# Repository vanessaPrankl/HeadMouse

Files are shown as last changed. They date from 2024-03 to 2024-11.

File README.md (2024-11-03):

# HeadMouse
 
This project provides hardware, enclosure and software for the head-motion based computermouse HeadMouse.



## Hardware
A BOM and PCB-files are provided in the hardware folder. A 600mAh LiPo-battery has been used for the prototyping, the battery only lasts for 3.5h in this case which is mainly caused by the high power consumption of the ESP32-S3-WROOM buetooth module. 



## Software
The following external libraries are utilized:
| Library | Provider | Licence |  
|------|----------|---------|
| [BleMouse](https://github.com/T-vK/ESP32-BLE-Mouse) | [T-vK](https://github.com/T-vK) | MIT License |
| [AdafruitBNO055](https://github.com/adafruit/Adafruit_BNO055) | [Adafruit](https://github.com/adafruit) | MIT License |
| [ESP32_TimerInterrupt](https://github.com/khoih-prog/ESP32TimerInterrupt) | [khoih-prog](https://github.com/khoih-prog) | MIT License|

Additionally, a HeadMouse library including major HeadMouse functions is provided. 



The hardware pins are configured in the hm_board_config_v1_0.hpp file of the headmouse library.
The default preferences are set in default_preferences.hpp (include folder of project).

## Enclosure
The enclosure consists of 2 3D-printed parts, 2 screws and according nuts for assembly and a sticky clip for mounting the deivce on the user's head. 



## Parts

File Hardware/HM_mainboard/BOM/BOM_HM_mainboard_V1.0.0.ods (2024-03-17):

Reference | Value | Digikey | Mouser | Reichelt | Menge | Datasheet
AC1 | LSM6DSOXTR |  | LSM6DSOXTR |  | 1 | https://www.st.com/resource/en/datasheet/lsm6dsox.pdf
C1, C4 | 4.7uF |  | 81-GRM188Z71A475KE5J |  | 2 | ~
C2, C3, C10, C19 | 1.0uF-25V-(+80/-20%) |  | 647-F921E105KPA |  | 4 | ~
C5, C6 | 15pF-1% |  | 80-C0603C150F8HAUTO |  | 2 | ~
C7 | 22uF |  | 81-GRM188R60J226ME0J |  | 1 | ~
C8, C9, C11-C18, C20 | 100nF | 1276-CL10B104KB8NNNLCT | 581-06035C104K4 |  | 11 | ~
D1 | 10BQ015 |  | 78-VS-10BQ015-M35BT |  | 1 | https://eu.mouser.com/ProductDetail/Vishay-Semiconductors/VS-10BQ015-M3-5BT?qs=asPD7ZL2j3VpzaHhlDLLKA%3D%3D&gad_source=1
D2 | WE-TVS-824015 |  | 710-824015 |  | 1 | https://www.we-online.com/components/products/datasheet/824015.pdf
D3, D4 | 155124RV73200 |  | 710-155124RV73200 |  | 2 | https://www.we-online.com/components/products/datasheet/155124RV73200.pdf
FL1 | WE-CNSW 744232090 |  | 710-744232090 |  | 1 | https://www.we-online.com/components/products/datasheet/744232090.pdf
J1 | JST PH2P ST90 |  |  | JST PH2P ST90 | 1 | https://www.reichelt.at/at/de/jst-stiftleiste-90-1x2-polig-ph-jst-ph2p-st90-p185056.html?PROVID=2807
J2 | USB4105-GF-A |  | 640-USB4105-GF-A |  | 1 | https://www.mouser.at/ProductDetail/GCT/USB4105-GF-A?qs=KUoIvG%2F9IlY%2FMLlBMpStpA%3D%3D&gad_source=1
J3 | Conn_01x04 |  | Stiftleiste, Raster: 2.54mm |  | 1 | ~
J4-J7 | 54-00174 | 839-54-00174CT |  |  | 4 | https://tensility.s3.amazonaws.com/uploads/pdffiles/54-00174.pdf?X-Amz-Expires=600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
Q1 | PMV27UPEAR | 4530-AS3401CT | 771-PMV27UPEAR |  | 1 | https://mm.digikey.com/Volume0/opasdata/d220001/medias/docus/2779/AS3401.pdf
R1 | 10k/1% |  | 660-RN73H1JT1002F100 |  | 1
R2 | 2k |  | 71-CRCW06032K00FKEAC |  | 1
R3, R4, R7, R12-R14 | 10k/1% |  | 660-RN73H1JT1002F100 |  | 6
R5, R6 | 5k1 |  | 791-RMC1/16K5101FTP |  | 2
R8-R11 | 120 |  | 603-RC0603FR-10120RL |  | 4
S1, S2 | SW_Push |  | 179-TS046643BK160SMT |  | 2 | https://www.mouser.at/datasheet/2/358/typ_6x6_mm_tact_switches-1275689.pdf
S3 | 450404015514 |  | 710-450404015514 |  | 1 | https://www.we-online.com/components/products/datasheet/450404015514.pdf
U1 | MCP73831-2 |  | 579-MCP73831T-2ACIOT |  | 1 | http://ww1.microchip.com/downloads/en/DeviceDoc/20001984g.pdf
U2 | TC1262-33 |  | 579-TC1262-3.3VDBTR |  | 1 | http://ww1.microchip.com/downloads/en/DeviceDoc/21373C.pdf
U3 | ESP32-S3-WROOM-1 |  | 356-ESP32-S3WRM1N8R2 |  | 1 | https://www.espressif.com/sites/default/files/documentation/esp32-s3-wroom-1_wroom-1u_datasheet_en.pdf
U4 | WE-TVS-824015043 |  | 710-824015043 |  | 1 | https://www.we-online.com/components/products/datasheet/824015043.pdf
U5 | MC6470 |  | 498-MC6470 |  | 1 | https://www.mouser.at/datasheet/2/821/MC6470_Datasheet_APS_048_0033v1_7_1-3003085.pdf
U6 | BNO055 | 828-1058 | 262-BNO055 |  | 1 | https://www.bosch-sensortec.com/media/boschsensortec/downloads/datasheets/bst-bno055-ds000.pdf
Y1 | 32.768 kHz |  | ABS07 |  | 1 | https://www.mouser.at/datasheet/2/3/ABS07-3080027.pdf

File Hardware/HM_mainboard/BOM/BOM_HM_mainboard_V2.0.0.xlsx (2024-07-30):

Reference | Value | Digikey | Mouser | Reichelt | 1 Platine | 3 Platinen | Bestand | Datasheet
C1, C4 | 4.7uF |  | 81-GRM188Z71A475KE5J |  | 2 | 6 | viele | ~
C2, C3, C10, C16 | 1.0uF |  | 647-F921E105KPA |  | 4 | 12 | 4 | ~
C5, C6 | 15pF-1% |  | 80-C0603C150F8HAUTO |  | 2 | 6 | 8 | ~
C7 | 22uF |  | 81-GRM188R60J226ME0J |  | 1 | 3 | viele | ~
C8, C9, C11, C12, C13, C14, C15, C17 | 100nF | 478-KGM15AR70J104KMTR-ND | 581-06035C104K4 |  | 8 | 24 | viele | ~
D1 | 10BQ015 |  | 78-VS-10BQ015-M35BT |  | 1 | 3 | 19 | https://eu.mouser.com/ProductDetail/Vishay-Semiconductors/VS-10BQ015-M3-5BT?qs=asPD7ZL2j3VpzaHhlDLLKA%3D%3D&gad_source=1
D2 | WE-TVS-824015 |  | 710-824015 |  | 1 | 3 | 10 | https://www.we-online.com/components/products/datasheet/824015.pdf
D3, D4 | 155124RV73200 |  | 710-155124RV73200 |  | 2 | 6 | 15 | https://www.we-online.com/components/products/datasheet/155124RV73200.pdf
FL1 | WE-CNSW 744232090 |  | 710-744232090 |  | 1 | 3 | 9 | https://www.we-online.com/components/products/datasheet/744232090.pdf
J1 | JST PH2P ST90 |  |  | JST PH2P ST90 | 1 | 3 | 3 | https://www.reichelt.at/at/de/jst-stiftleiste-90-1x2-polig-ph-jst-ph2p-st90-p185056.html?PROVID=2807
J2 | USB4105-GF-A |  | 640-USB4105-GF-A |  | 1 | 3 | 9 | https://www.usb.org/sites/default/files/documents/usb_type-c.zip
J4, J6, J7 | 54-00174 | 839-54-00174CT |  |  | 3 | 9 | 0 | https://tensility.s3.amazonaws.com/uploads/pdffiles/54-00174.pdf?X-Amz-Expires=600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
J5 | 9159005551906 | 478-8739-1-ND | 581-009159005551906 |  | 1 | 3 | 0 | ~
Q1 | PMOS AS3401 | 4530-AS3401CT | 771-PMV27UPEAR |  | 1 | 3 | viele | https://ngspice.sourceforge.io/docs/ngspice-manual.pdf
R1, R9, R14, R15 | 10k |  | 660-RN73H1JT1002F100 |  | 4 | 12 | 0
R2 | 2k |  | 71-CRCW06032K00FKEAC |  | 1 | 3 | viele
R3, R4 | 100k |  | 667-ERJ-PA3J121V |  | 2 | 6 | 2
R5, R6 | 5k1 |  | 791-RMC1/16K5101FTP |  | 2 | 6 | viele
R7 | 4k7 |  | 660-RN73H1JT4701F100 |  | 1 | 3 | 4
R8 | 1k8 |  | 667-ERA-3AEB182V |  | 1 | 3 | 0
R10-R13 | 120 |  | 667-ERJ-PA3J121V |  | 4 | 12 | viele
S1, S2 | SW_Push |  | 179-TS046643BK160SMT |  | 2 | 6 | viele | https://www.mouser.at/datasheet/2/358/typ_6x6_mm_tact_switches-1275689.pdf
S3 | 450404015514 |  | 710-450404015514 |  | 1 | 3 | 9 | https://www.we-online.com/components/products/datasheet/450404015514.pdf
SW1 | SKHHLQA010 | -- | 688-SKHHLQ |  | 1 | 3 | 0 | ~
U1 | MCP73831-2 |  | 579-MCP73831T-2ACIOT |  | 1 | 3 | 21 | http://ww1.microchip.com/downloads/en/DeviceDoc/20001984g.pdf
U2 | TC1262-33 |  | 579-TC1262-3.3VDBTR |  | 1 | 3 | 19 | http://ww1.microchip.com/downloads/en/DeviceDoc/21373C.pdf
U3 | ESP32-S3-WROOM-1 |  | 356-ESP32-S3WRM1N8R2 |  | 1 | 3 | 3 | https://www.espressif.com/sites/default/files/documentation/esp32-s3-wroom-1_wroom-1u_datasheet_en.pdf
U4 | WE-TVS-824015043 |  | 710-824015043 |  | 1 | 3 | 10 | https://www.we-online.com/components/products/datasheet/824015043.pdf
U5 | BNO055 | 828-1058 | 262-BNO055 |  | 1 | 3 | 0 | BNO055
Y1 | 32.768 kHz |  | 815-S07AIG-32.7687DT |  | 1 | 3 | 9 | https://www.mouser.at/datasheet/2/3/ABS07-3080027.pdf

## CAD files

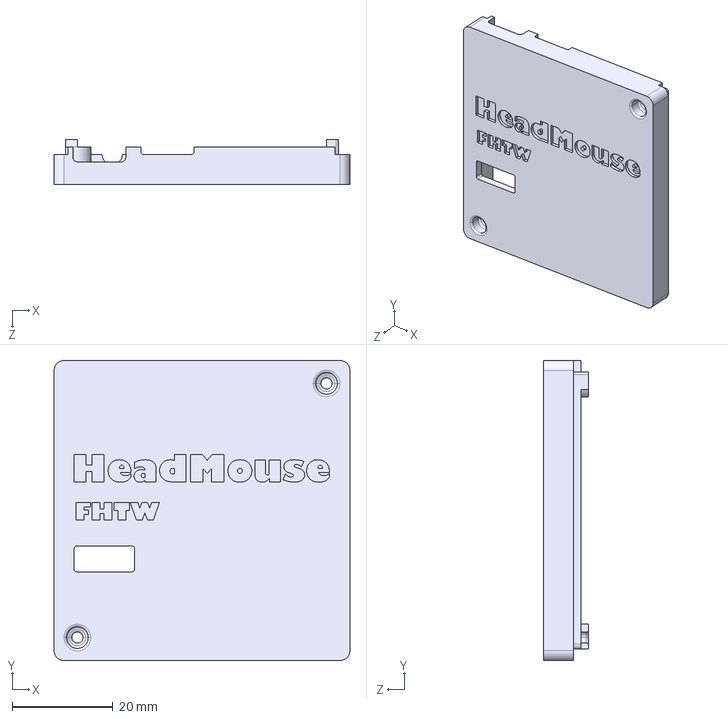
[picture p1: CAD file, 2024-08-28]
Enclosure/3D_Print/Case_top.STEP
58.7 x 59.5 x 9.00 mm

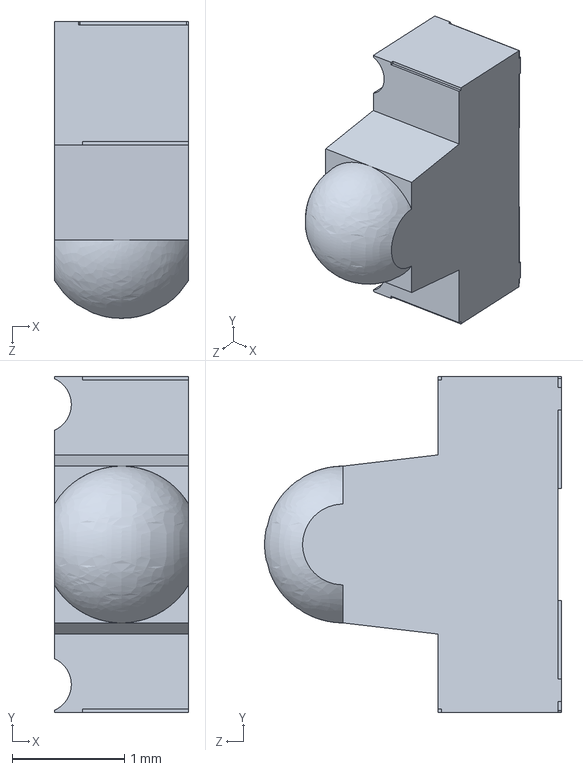
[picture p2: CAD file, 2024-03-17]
Hardware/Reference_designs/FlipMouse/step/SFH4045N.step
1.20 x 3.00 x 2.65 mm

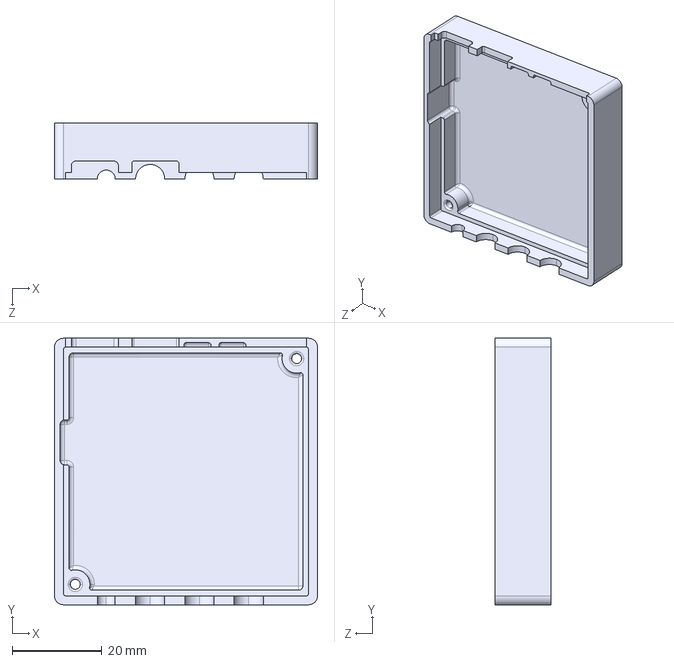
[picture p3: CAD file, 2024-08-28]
Enclosure/3D_Print/Case_bottom.STEP
58.7 x 59.5 x 12.5 mm

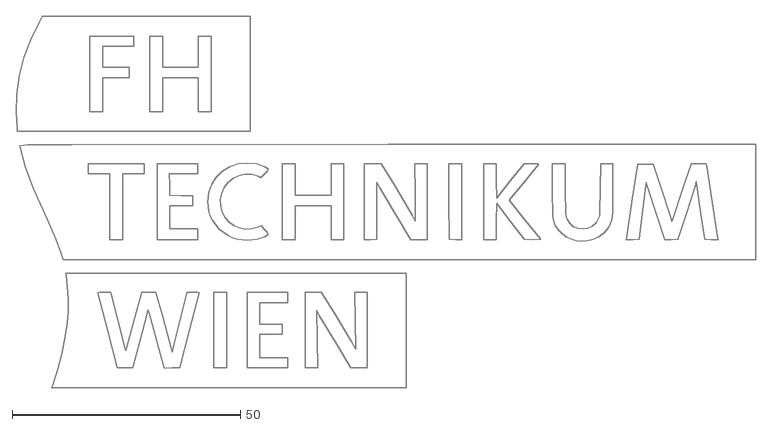
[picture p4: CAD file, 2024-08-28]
Enclosure/FHTW_Logo.dxf
161.9 x 81.4

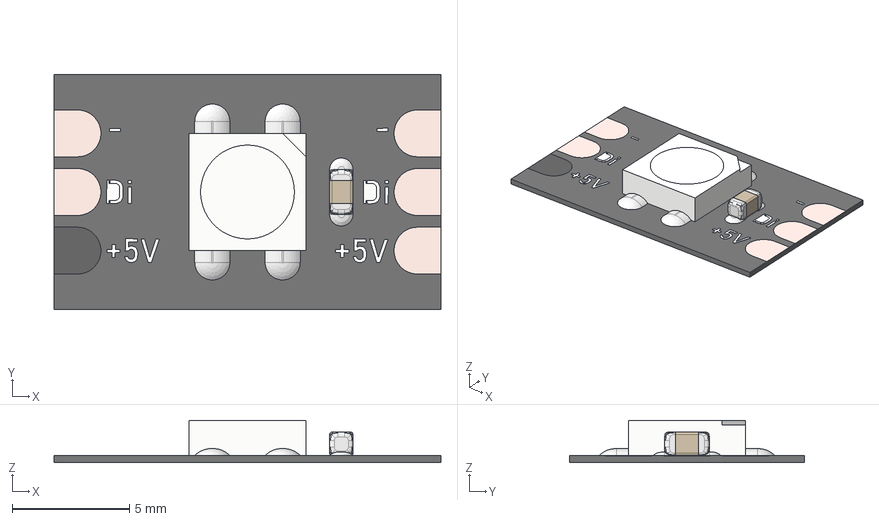
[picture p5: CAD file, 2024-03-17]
Hardware/Reference_designs/FlipMouse/step/NP.step
16.5 x 10.0 x 1.80 mm

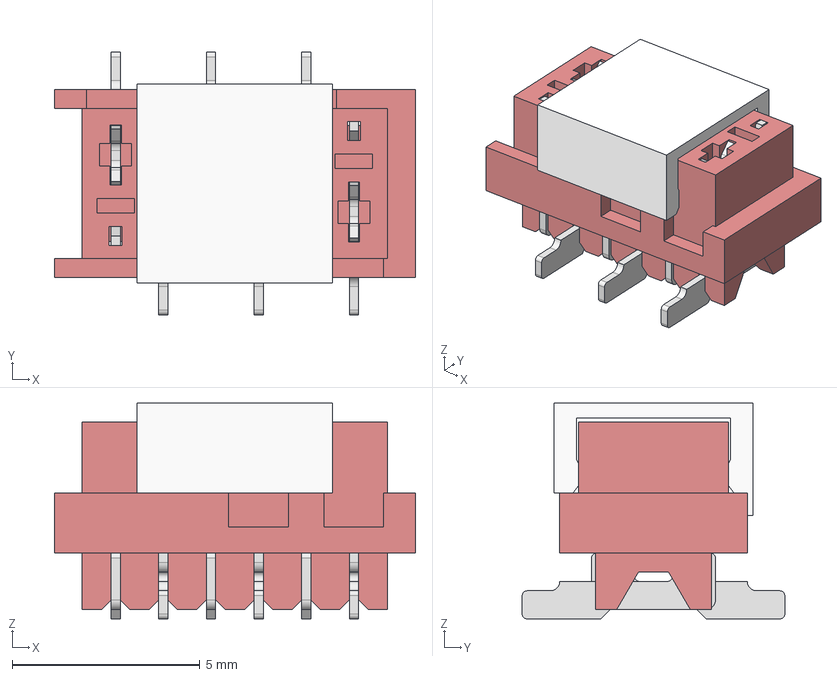
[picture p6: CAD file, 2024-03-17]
Hardware/Reference_designs/FlipMouse/step/690367280676.step
9.62 x 7.00 x 5.75 mm

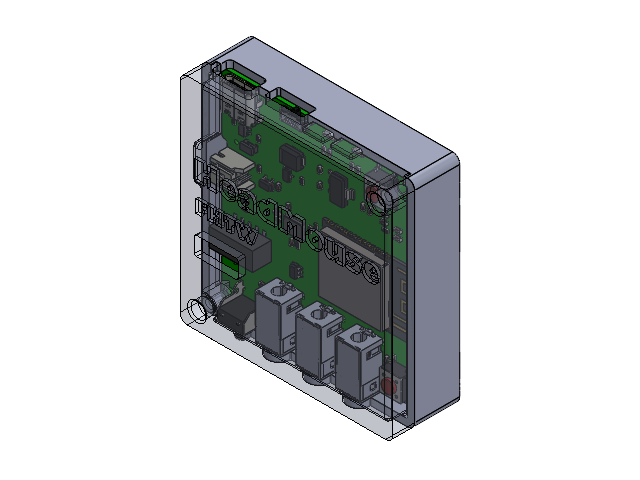
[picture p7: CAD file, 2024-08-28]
Enclosure/Enclosure_Assembly.SLDASM
Case_top
Case_bottom
HM_mainboard

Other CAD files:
Enclosure/3D_Print/Case_bottom.3mf
Enclosure/3D_Print/Case_top.3mf
Enclosure/Case_bottom.SLDPRT
Enclosure/Case_top.SLDPRT

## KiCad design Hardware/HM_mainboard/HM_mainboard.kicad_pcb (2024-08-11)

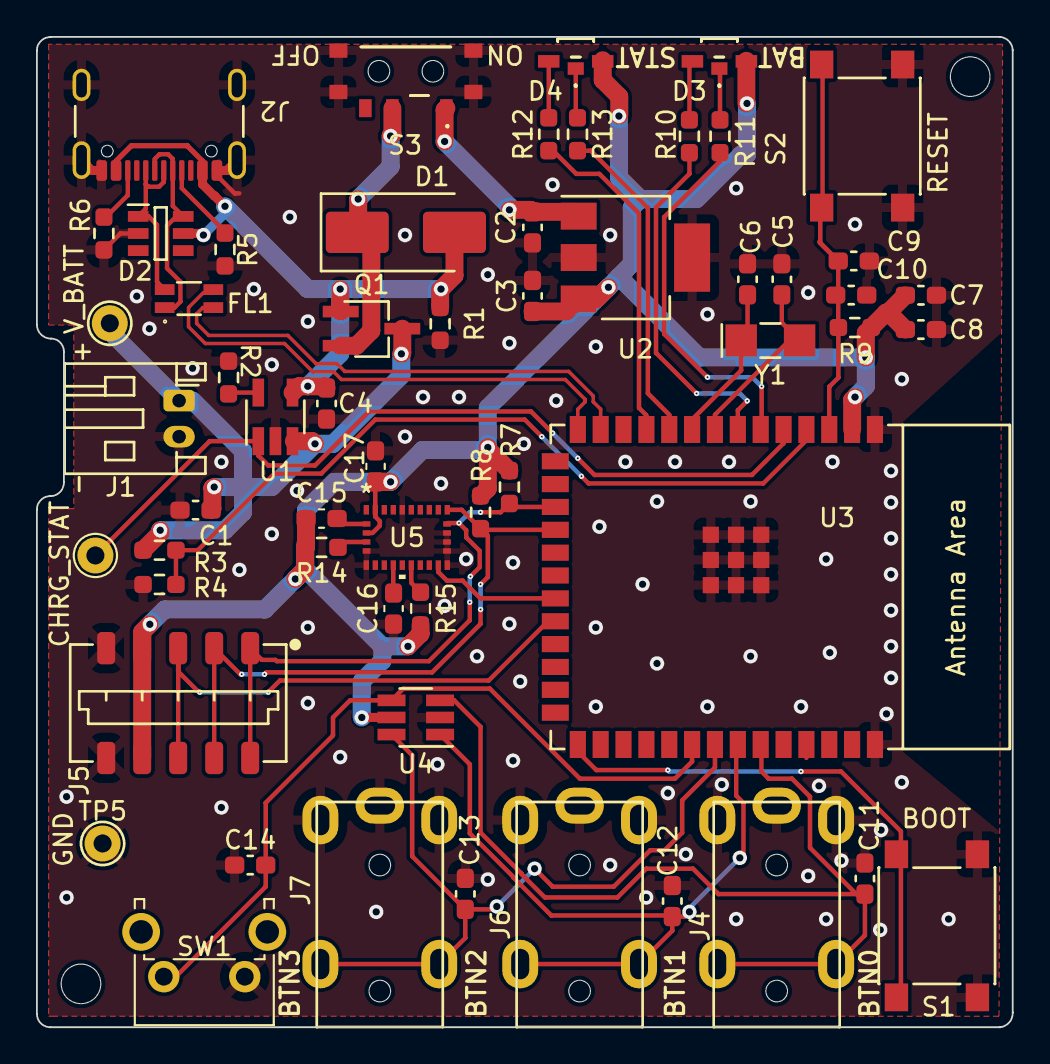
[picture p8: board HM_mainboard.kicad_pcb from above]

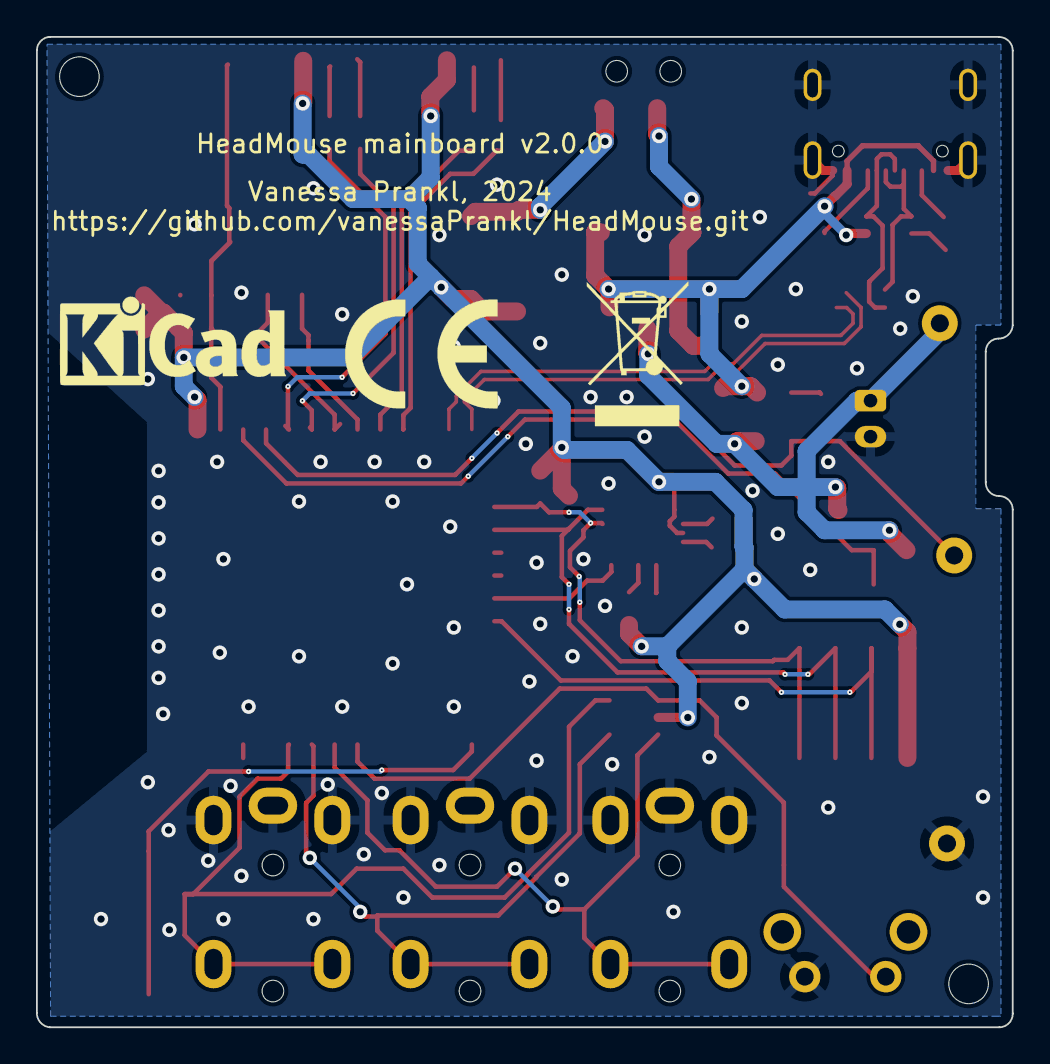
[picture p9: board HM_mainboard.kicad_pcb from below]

Board: 2 copper layers, 54.2 x 55.0 mm, 63 parts (3 on the bottom side), 38 nets.

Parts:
C1, C4: 4.7uF; C_0603_1608Metric_Pad1.08x0.95mm_HandSolder
C2, C3, C10, C16: 1.0uF; C_0603_1608Metric_Pad1.08x0.95mm_HandSolder
C5, C6: 15pF-1%; C_0603_1608Metric_Pad1.08x0.95mm_HandSolder
C7: 22uF; C_0603_1608Metric_Pad1.08x0.95mm_HandSolder
C8, C9, C11, C12, C13, C14, C15, C17: 100nF; C_0603_1608Metric_Pad1.08x0.95mm_HandSolder
D1: 10BQ015; D_SMB_Handsoldering
D2: WE-TVS-824015; SOT95P280X145-6N
D3, D4: 155124RV73200
FL1: WE-CNSW 744232090; WE-CNSW-SMD
H1, H2: MountingHole; MountingHole_2.2mm_M2_ISO7380
J1: JST PH2P ST90; JST_PH_S2B-PH-K_1x02_P2.00mm_Horizontal
J2: USB4105-GF-A; USB_C_Receptacle_GCT_USB4105-xx-A_16P_TopMnt_Horizontal
J4, J6, J7: 54-00174
J5: 009159005551906
LOGO1: Logo_HM; LOGO_HM_V2.0.0
LOGO2: Logo_KiCAD; KiCad-Logo_5mm_SilkScreen
LOGO3: Logo_CE; CE-Logo_8.5x6mm_SilkScreen
LOGO4: Logo_WEEE; WEEE-Logo_5.6x8mm_SilkScreen
Q1: PMOS AS3401; TSOT-23_HandSoldering
R1, R9, R14, R15: 10k; R_0603_1608Metric_Pad0.98x0.95mm_HandSolder
R2: 2k; R_0603_1608Metric_Pad0.98x0.95mm_HandSolder
R3, R4: 100k; R_0603_1608Metric_Pad0.98x0.95mm_HandSolder
R5, R6: 5k1; R_0603_1608Metric_Pad0.98x0.95mm_HandSolder
R7: 4k7; R_0603_1608Metric_Pad0.98x0.95mm_HandSolder
R8: 1k8; R_0603_1608Metric_Pad0.98x0.95mm_HandSolder
R10, R11, R12, R13: 120; R_0603_1608Metric_Pad0.98x0.95mm_HandSolder
S1, S2: SW_Push; SW_Push_1P1T_NO_6x6mm_H9.5mm
S3: 450404015514
SW1: SKHHLQA010; SW_Tactile_SPST_Angled_PTS645Vx58-2LFS
TP2, TP4, TP5: TestPoint_Probe; TestPoint_THTPad_D2.0mm_Drill1.0mm
U1: MCP73831-2; SOT-23-5_HandSoldering
U2: TC1262-33; SOT-223-3_TabPin2
U3: ESP32-S3-WROOM-1
U4: WE-TVS-824015043; SOT-23-6_Handsoldering
U5: BNO055; QFN_BNO055_BOS
Y1: 32.768 kHz; Crystal_SMD_MicroCrystal_CC7V-T1A-2Pin_3.2x1.5mm_HandSolder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

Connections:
3.3V: C3.1, C7.2, C8.2, C15.1, C17.1, D3.2 (A), D4.2 (A), J5.4, R7.2, R8.2, R9.2, R14.2, R15.2, U2.3 (VO), U3.2 (3V3), U4.5 (VBUS), U5.3 (VDD), U5.28 (VDDIO)
/BAT_CHRG_STATUS: TP4.1, U1.1 (STAT), U3.5 (GPIO5/TOUCH5/ADC1_CH4)
/BNO55_INT: U3.21 (GPIO13/TOUCH13/ADC2_CH2/FSPIQ/FSPIIO7/S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), U5.14 (INT)
/BTN_1: C11.1, J4.4, J4.5, U3.35 (MTMS/GPIO42), U4.3 (I/O2)
/BTN_2: C12.1, J6.4, J6.5, U3.34 (MTDI/GPIO41/CLK_OUT1), U4.1 (I/O1)
/BTN_3: C13.1, J7.4, J7.5, U3.33 (MTDO/GPIO40/CLK_OUT2), U4.6 (I/O4)
/BTN_4: C14.1, SW1.2, U3.32 (MTCK/GPIO39/CLK_OUT3/SUBSPICS1), U4.4 (I/O3)
/Battery_and_Power_Managment/V_IN: C2.1, S3.1, U2.1 (VI)
/Battery_and_Power_Managment/V_PWR_SWITCH: D1.1 (C), Q1.2 (S), S3.2
/I2C_SCL: J5.1, R7.1, U3.17 (GPIO9/TOUCH9/ADC1_CH8/FSPIHD/SUBSPIHD), U5.19 (COM1)
/I2C_SDA: J5.2, R8.1, U3.18 (GPIO10/TOUCH10/ADC1_CH9/FSPICS0/FSPIIO4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), U5.20 (COM0)
/LED_BAT_G: R10.1, U3.7 (GPIO7/TOUCH7/ADC1_CH6)
/LED_BAT_R: R11.1, U3.6 (GPIO6/TOUCH6/ADC1_CH5)
/LED_STAT_G: R12.1, U3.11 (GPIO18/U1RXD/ADC2_CH7/CLK_OUT3)
/LED_STAT_R: R13.1, U3.10 (GPIO17/U1TXD/ADC2_CH6)
/MPRLS_INT: J5.3, U3.22 (GPIO14/TOUCH14/ADC2_CH3/FSPIWP/FSPIDQS/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)
/Microcontroller - ESP32-S3-WROOM/BOOT: S1.2, U3.27 (GPIO0/BOOT)
/Microcontroller - ESP32-S3-WROOM/EN: C9.2, C10.2, R9.1, S2.2, U3.3 (EN)
/Microcontroller - ESP32-S3-WROOM/USB_C_D+: FL1.3, U3.14 (GPIO20/U1CTS/ADC2_CH9/CLK_OUT1/USB_D+)
/Microcontroller - ESP32-S3-WROOM/USB_C_D-: FL1.2, U3.13 (GPIO19/U1RTS/ADC2_CH8/CLK_OUT2/USB_D-)
/V_BAT_MEASURE: R3.1, R4.2, U3.4 (GPIO4/TOUCH4/ADC1_CH3)
GND: C1.2, C2.2, C3.2, C4.2, C5.1, C6.1, C7.1, C8.1, C9.1, C10.1, C11.2, C12.2, C13.2, C14.2, C15.2, C16.1, C17.2, D2.2 (GND), J1.2, J2.A1 (GND), J2.A12 (GND), J2.B1 (GND), J2.B12 (GND), J2.S1 (SHIELD), J4.1, J4.2, J4.3, J5.5, J6.1, J6.2, J6.3, J7.1, J7.2, J7.3, R1.1, R2.1, R4.1, R5.1, R6.1, S1.1, S2.1, S3.MP1, S3.MP2, S3.MP3, S3.MP4, SW1.1, TP5.1, U1.2 (V_{SS}), U2.2 (GND), U3.1 (GND), U3.40 (GND), U3.41 (GND), U4.2 (GND), U5.2 (GND), U5.5 (PS1), U5.6 (PS0), U5.15 (Pin15), U5.16 (Pin16), U5.17 (COM3), U5.18 (COM2), U5.25 (GNDIO)
unnamed: D2.1 (I/O), FL1.4, J2.A6 (D+), J2.B6 (D+)
unnamed: D2.6 (I/O), FL1.1, J2.A7 (D-), J2.B7 (D-)
unnamed: D3.1 (K1), R11.2
unnamed: D3.3 (K2), R10.2
unnamed: D4.1 (K1), R13.2
unnamed: D4.3 (K2), R12.2
unnamed: J2.A5 (CC1), R5.2
unnamed: J2.B5 (CC2), R6.2
unnamed: R2.2, U1.5 (PROG)
unnamed: C5.2, U3.8 (GPIO15/U0RTS/ADC2_CH4/XTAL_32K_P), Y1.2
unnamed: C6.2, U3.9 (GPIO16/U0CTS/ADC2_CH5/XTAL_32K_N), Y1.1
unnamed: C16.2, U5.9 (CAP)
unnamed: R14.1, U5.4 (NBOOT_LOAD_PIN)
unnamed: R15.1, U5.11 (NRESET)
V_BATT: C1.1, J1.1, Q1.3 (D), R3.2, TP2.1, U1.3 (V_{BAT})
V_USB: C4.1, D1.2 (A), D2.5 (VDD), J2.A4 (VBUS), J2.A9 (VBUS), J2.B4 (VBUS), J2.B9 (VBUS), Q1.1 (G), R1.2, U1.4 (V_{DD})

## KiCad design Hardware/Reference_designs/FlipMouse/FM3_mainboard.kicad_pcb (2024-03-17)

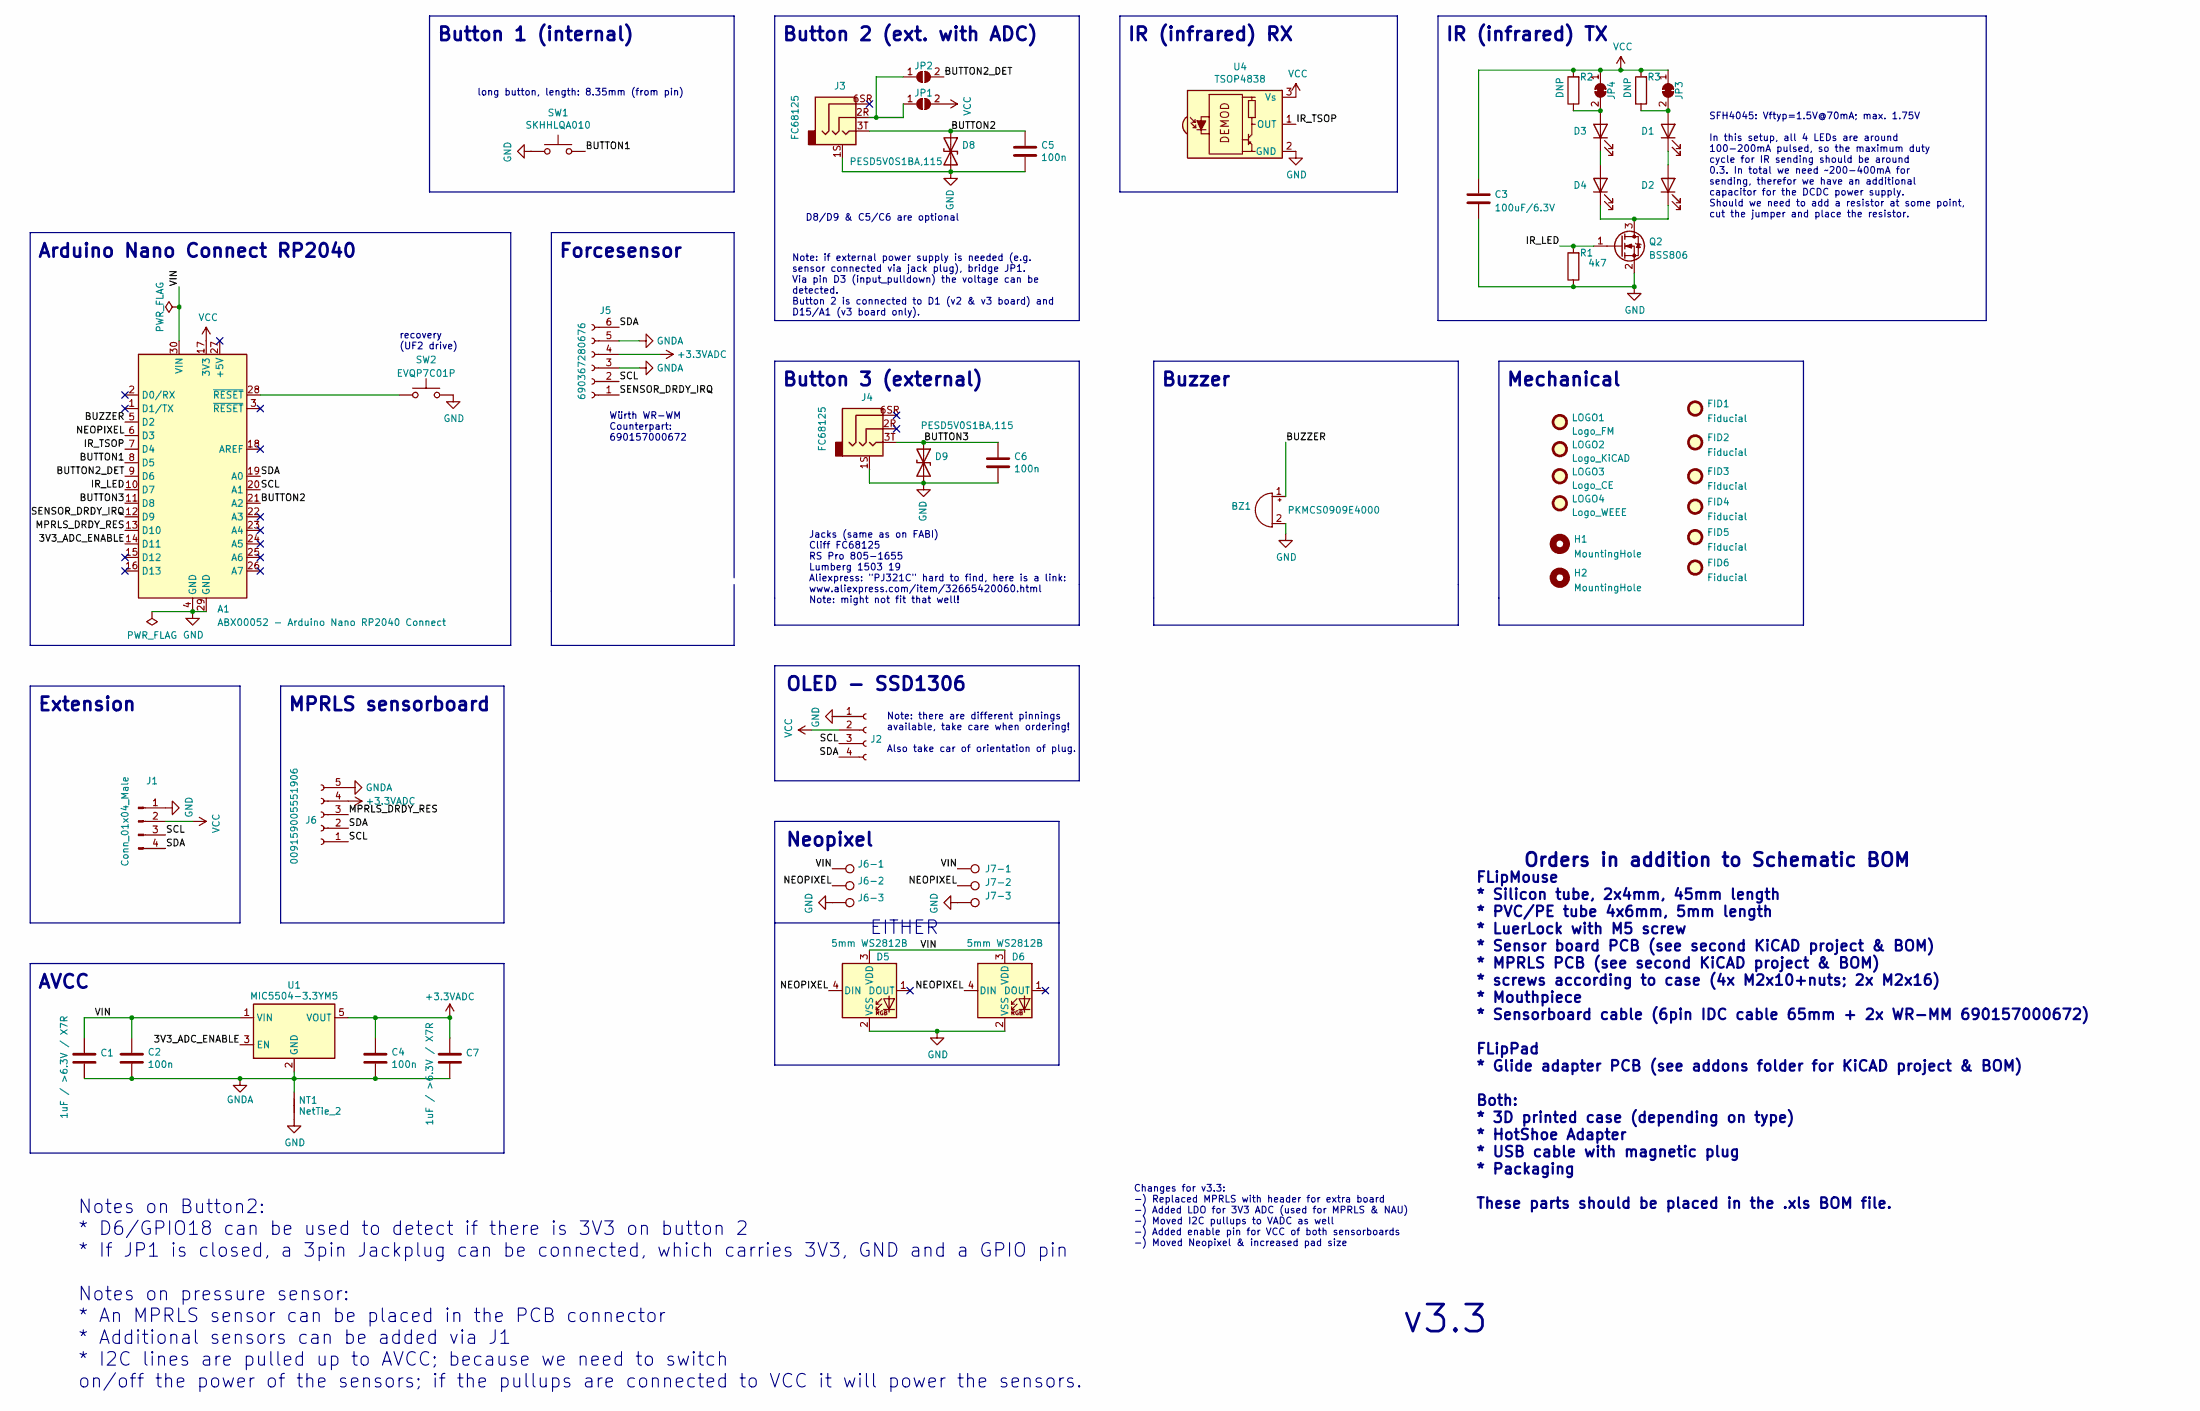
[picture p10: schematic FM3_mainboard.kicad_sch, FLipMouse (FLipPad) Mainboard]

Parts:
A1: ABX00052 - Arduino Nano RP2040 Connect; NANO_33_Footprint_SMD_Castell_AlignmentHoles; Digikey 1050-ABX00052-ND
BZ1: PKMCS0909E4000; Buzzer_Murata_PKMCS0909E; Digikey 490-9647-1-ND
C1, C7: 1uF / >6.3V / X7R; C_0603_1608Metric; Digikey 1276-1019-1-ND
C2, C4, C5, C6: 100n; C_0603_1608Metric; Digikey 1276-CL10B104KB8NNNLCT-ND
C3: 100uF/6.3V; C_1210_3225Metric; Digikey 1276-1092-1-ND
D1, D2: SFH4045; SFH4045N; Farnell 2981752
D3, D4: SFH4045; SFH4045N; Digikey 475-3047-1-ND
D5, D6: 5mm WS2812B; NeopixelTHT; Digikey 1568-1202-ND
D8, D9: PESD5V0S1BA,115; D_SOD-323; Digikey 1727-3837-1-ND
FID1, FID2, FID3, FID4, FID5, FID6: Fiducial; Fiducial_0.5mm_Mask1mm; Digikey DNP
H1, H2: MountingHole; MountingHole_2.2mm_M2_ISO7380; Digikey DNP
J1: Conn_01x04_Male; pressure_sensor; Digikey DNP
J2: SSM-104-L-SV; PinSocket_1x04_P2.54mm_Vertical_SMD_Pin1Right; Digikey S5596-ND
J3: FC68125; Digikey 3185-FC68125-ND
J4: FC68125; Farnell 2309468
J5: 690367280676; Digikey 732-1965-1-ND
J6: 009159005551906; Digikey 478-8739-1-ND
J6-1, J6-2, J6-3, J7-1, J7-2, J7-3: TestPoint; SolderWirePad_1x01_SMD_1x2mm; Digikey DNP
JP1, JP2: SolderJumper_2_Open; SolderJumper-2_P1.3mm_Open_RoundedPad1.0x1.5mm; Digikey DNP
JP3, JP4: SolderJumper_2_Bridged; SolderJumper-2_P1.3mm_Bridged_RoundedPad1.0x1.5mm; Digikey DNP
LOGO1: Logo_FM; flipmouse_11x5; Digikey DNP
LOGO2: Logo_KiCAD; KiCad-Logo_5mm_SilkScreen; Digikey DNP
LOGO3: Logo_CE; CE-Logo_8.5x6mm_SilkScreen; Digikey DNP
LOGO4: Logo_WEEE; WEEE-Logo_5.6x8mm_SilkScreen; Digikey DNP
NT1: NetTie_2; NetTie-2_SMD_Pad0.5mm; Digikey DNP
Q2: BSS806; SOT-23; Digikey BSS806NH6327XTSA1CT-ND
R1: 4k7; R_0603_1608Metric; Farnell 3994558
R2, R3: DNP; R_0603_1608Metric; Farnell 3994558
SW1: SKHHLQA010; SW_Tactile_SPST_Angled_PTS645Vx58-2LFS; Farnell 2056827
SW2: EVQP7C01P; SW_SPST_EVQP7C; Digikey P16765CT-ND
U1: MIC5504-3.3YM5; SOT-23-5; Digikey 576-4764-1-ND
U4: TSOP4838; Vishay_MOLD-3Pin; Farnell 4913190

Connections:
+3.3VADC: C4.1, C7.1, J5.4, J6.4, U1.5 (VOUT)
/3V3_ADC_ENABLE: A1.14 (D11), U1.3 (EN)
/BUTTON1: A1.8 (D5), SW1.2
/BUTTON2: A1.21 (A2), C5.1, D8.1 (A1), J3.3T
/BUTTON2_DET: A1.9 (D6), JP2.2 (B)
/BUTTON3: A1.11 (D8), C6.1, D9.1 (A1), J4.3T
/BUZZER: A1.5 (D2), BZ1.1 (-)
/IR_LED: A1.10 (D7), Q2.1 (G), R1.2
/IR_TSOP: A1.7 (D4), U4.1 (OUT)
/MPRLS_DRDY_RES: A1.13 (D10), J6.3
/NEOPIXEL: A1.6 (D3), D5.4 (DIN), D6.4 (DIN), J6-2.1, J7-2.1
/SCL: A1.20 (A1), J1.3, J2.3, J5.2, J6.1
/SDA: A1.19 (A0), J1.4, J2.4, J5.6, J6.2
/SENSOR_DRDY_IRQ: A1.12 (D9), J5.1
/VIN: A1.30 (VIN), C1.1, C2.1, D5.3 (VDD), D6.3 (VDD), J6-1.1, J7-1.1, U1.1 (VIN)
GND: A1.4 (GND), A1.29 (GND), BZ1.2 (+), C3.2, C5.2, C6.2, D5.2 (VSS), D6.2 (VSS), D8.2 (A2), D9.2 (A2), J1.1, J2.1, J3.1S, J4.1S, J6-3.1, J7-3.1, NT1.1, Q2.2 (S), R1.1, SW1.1, SW2.1, U4.2 (GND)
GNDA: C1.2, C2.2, C4.2, C7.2, J5.3, J5.5, J6.5, NT1.2, U1.2 (GND)
unnamed: A1.28 (~RESET), SW2.2
unnamed: D1.2 (A), JP3.2 (B), R3.1
unnamed: D1.1 (K), D2.2 (A)
unnamed: D2.1 (K), D4.1 (K), Q2.3 (D)
unnamed: D3.2 (A), JP4.2 (B), R2.1
unnamed: D3.1 (K), D4.2 (A)
unnamed: J3.2R, JP1.1 (A), JP2.1 (A)
VCC: A1.17 (3V3), C3.1, J1.2, J2.2, JP1.2 (B), JP3.1 (A), JP4.1 (A), R2.2, R3.2, U4.3 (Vs)

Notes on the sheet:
Neopixel
Buzzer
OLED - SSD1306
Würth WR-WM Counterpart: 690157000672
v3.3
EITHER
AVCC
Changes for v3.3: -) Replaced MPRLS with header for extra board -) Added LDO for 3V3 ADC (used for MPRLS & NAU) -) Moved I2C pullups to VADC as well -) Added enable pin for VCC of both sensorboards -) Moved Neopixel & increased pad size
MPRLS sensorboard
FLipMouse * Silicon tube, 2x4mm, 45mm length * PVC/PE tube 4x6mm, 5mm length * LuerLock with M5 screw * Sensor board PCB (see second KiCAD project & BOM) * MPRLS PCB (see second KiCAD project & BOM) * screws according to case (4x M2x10+nuts; 2x M2x16) * Mouthpiece * Sensorboard cable (6pin IDC cabl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
long button, length: 8.35mm (from pin)
Note: there are different pinnings available, take care when ordering! Also take car of orientation of plug.
Note: if external power supply is needed (e.g. sensor connected via jack plug), bridge JP1. Via pin D3 (input_pulldown) the voltage can be detected. Button 2 is connected to D1 (v2 & v3 board) and D15/A1 (v3 board only).
IR (infrared) RX
Jacks (same as on FABI) Cliff FC68125 RS Pro 805-1655 Lumberg 1503 19 Aliexpress: "PJ321C" hard to find, here is a link: www.aliexpress.com/item/32665420060.html Note: might not fit that well!
Button 1 (internal)
Orders in addition to Schematic BOM
Button 2 (ext. with ADC)
SFH4045: Vftyp=1.5V@70mA; max. 1.75V In this setup, all 4 LEDs are around 100-200mA pulsed, so the maximum duty cycle for IR sending should be around 0.3. In total we need ~200-400mA for sending, therefor we have an additional capacitor for the DCDC power supply. Should we need to add a resistor at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
Extension
D8/D9 & C5/C6 are optional
Mechanical
Forcesensor
Arduino Nano Connect RP2040
Notes on Button2: * D6/GPIO18 can be used to detect if there is 3V3 on button 2 * If JP1 is closed, a 3pin Jackplug can be connected, which carries 3V3, GND and a GPIO pin Notes on pressure sensor: * An MPRLS sensor can be placed in the PCB connector * Additional sensors can be added via J1 * I2C l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
Button 3 (external)
IR (infrared) TX
recovery (UF2 drive)

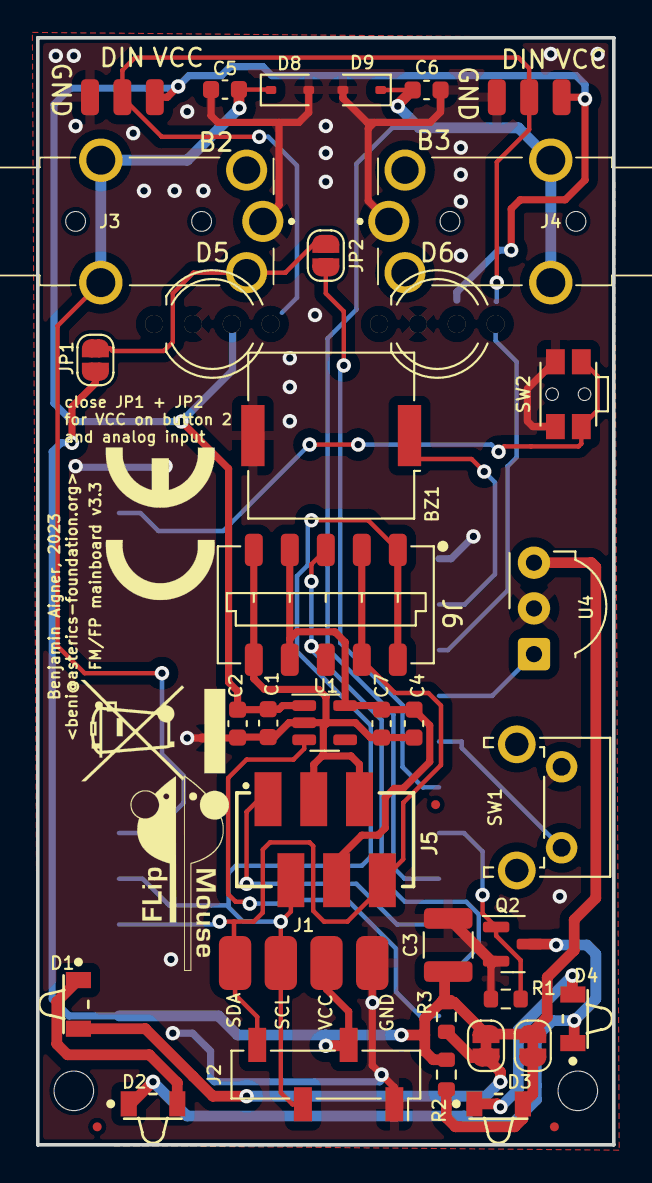
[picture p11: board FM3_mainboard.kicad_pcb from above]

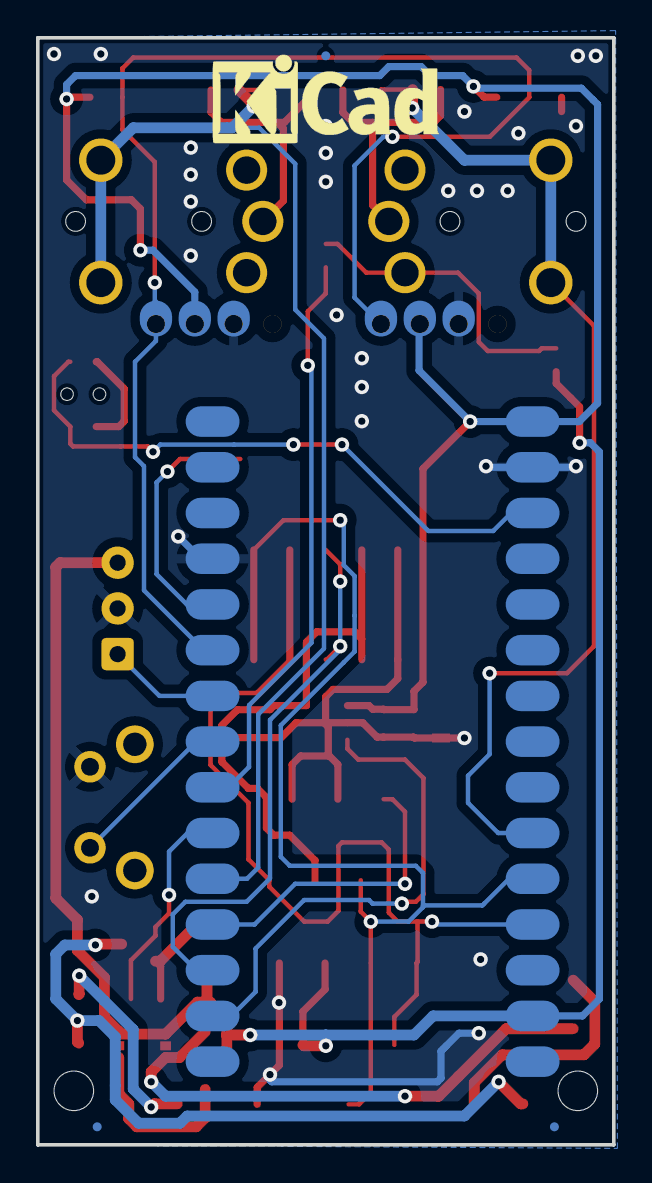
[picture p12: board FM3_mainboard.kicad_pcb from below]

Board: 2 copper layers, 32.0 x 61.5 mm, 54 parts (5 on the bottom side), 25 nets.

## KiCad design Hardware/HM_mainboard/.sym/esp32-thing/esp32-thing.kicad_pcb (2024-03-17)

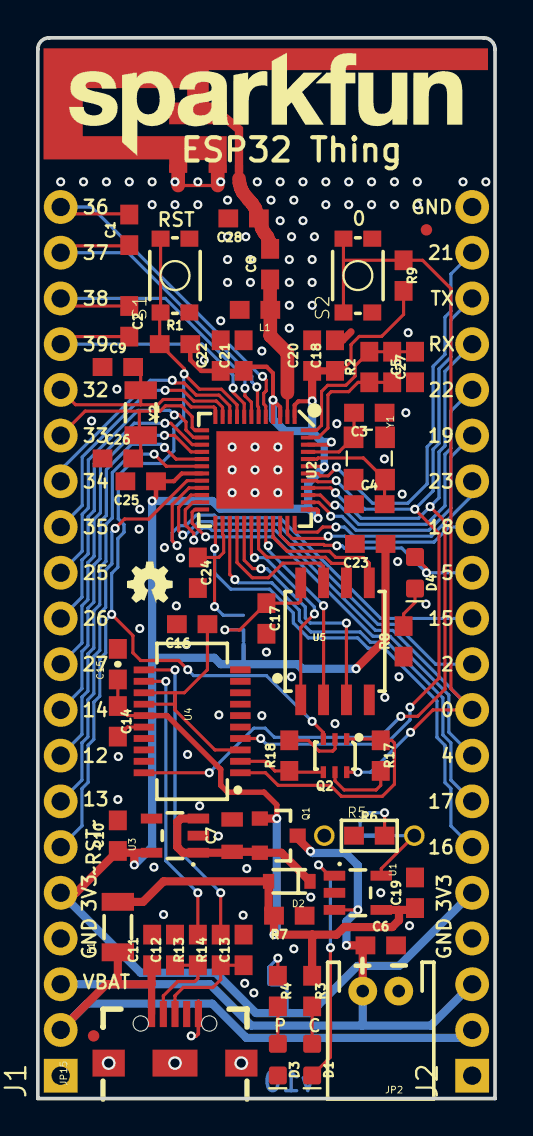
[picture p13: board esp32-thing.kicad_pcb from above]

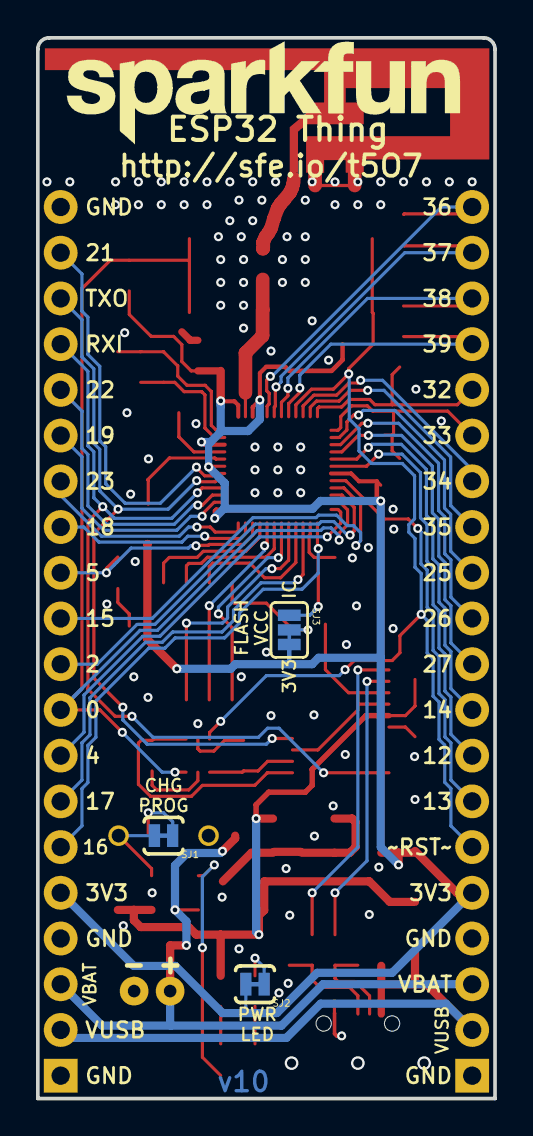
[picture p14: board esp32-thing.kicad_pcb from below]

Board: 2 copper layers, 25.4 x 58.9 mm, 72 parts (4 on the bottom side), 66 nets.

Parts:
C1, C2: 270pF; 0603
C3, C4: 10pF; 0603
C5: 10nF; 0603
C6, C19: 4.7uF; 0603
C7: 1.0uF; 0805
C8: 5.6pF; 0603
C9, C26: 15pF; 0603
C10: 2.2uF; 0603
C11, C14, C16, C17, C20, C21, C23, C25: 0.1uF; 0603
C12, C13: 47pF; 0603
C15: 4.7uF; 0603-CAP
C18: 100pF; 0603
C22: 10uF; 0603
C24: 1.0uF; 0603
C27: 3.0nF; 0603
C28: 2.4pF; 0603
D1: Yellow; LED-0603
D2: BAT20J; SOD-323
D3: RED; LED-0603
D4: BLUE; LED-0603
E1: ANTENNA; TRACE_ANTENNA_2.4GHZ_25.7MM_TUNED
F1: 500mA; PTC-1206
FD1, FD2: FIDUCIALUFIDUCIAL; MICRO-FIDUCIAL
FRAME1: FRAME-LEDGER; CREATIVE_COMMONS
J1, J2: 1X20_NOSILK
JP2: LiPo; JST-2-PTH
JP15: USB-B-MICRO-SMD_V03
L1: 2.7nH; 0603
LOGO1, LOGO3: SFE_LOGO_NAME.2_INCH; SFE_LOGO_NAME_.2
LOGO2: OSHW-LOGOMINI; OSHW-LOGO-MINI
Q1: 2.5A/30V; SOT23-3
Q2: MBT3904DW1T1; SC70-6
R1, R7, R9, R17, R18: 10k; 0603
R2: 20k; 0603
R3, R4: 1K; 0603
R5: DNP; 1_6W-RES
R6: 2.0k; 0603
R8: 330; 0603
R13, R14: 27; 0603
S1: RESET; TACTILE_SWITCH_SMD_4.6X2.8MM
S2: BTN-0; TACTILE_SWITCH_SMD_4.6X2.8MM
SJ1, SJ2: JUMPER-PAD-2-NC_BY_TRACE; PAD-JUMPER-2-NC_BY_TRACE_YES_SILK
SJ3: PAD-JUMPER-3-2OF3_NC_BY_TRACE_YES_SILK_FULL_BOX
U1: MCP73831; SOT23-5
U2: ESP3212; QFN48-0.4MM
U3: AP2112K-3.3V; SOT23-5
U4: FT231XS; SSOP20_L
U5: W25Q32FVSS; SOIC-8
Y1: 26MHz; CRYSTAL-SMD-3.2X2.5
Y2: 32.768kHz; CRYSTAL-SMD-3.2X1.5MM

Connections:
0: J2.9, Q2.6, R9.1, S2.3, S2.4, U2.23
2: J2.10, U2.22
3.3V: C10.1, C18.1, C20.1, C21.1, C22.1, C23.1, C25.1, J1.5, J2.5, R1.2, R9.2, SJ2.2, SJ3.3, U2.1, U2.3, U2.4, U2.19, U2.37, U2.43, U2.46, U3.5
3.3V_F: C16.1, U4.3, U4.13, U4.14
4: J2.8, U2.24
5: D4.A, J2.12, U2.34
12: J1.8, U2.18
13: J1.7, U2.20
14: J1.9, U2.17
15: J2.11, U2.21
16: J2.6, U2.25
17: J2.7, U2.27
18: J2.13, U2.35
19: J2.15, U2.38
21: J2.19, U2.42
22: J2.16, U2.39
23: J2.14, U2.36
25: J1.12, U2.14
26: J1.11, U2.15
27: J1.10, U2.16
32K_XN: C26.2, J1.15, U2.13, Y2.P$2
32K_XP: C9.2, J1.16, U2.12, Y2.P$1
34: J1.14, U2.10
35: J1.13, U2.11
36: C1.2, J1.20, U2.5
37: C1.1, J1.19, U2.6
38: C2.1, J1.18, U2.7
39: C2.2, J1.17, U2.8
CAP_10N: C5.2, C27.1, R2.2, U2.48
CHIP_PU: J1.6, Q2.3, R1.1, S1.3, S1.4, U2.9
D+: C13.1, JP15.D+, R14.1
D-: C12.1, JP15.D-, R13.1
DTR: Q2.1, R17.1, U4.1
FLASH_SCK: U2.31, U5.6
FLASH_SCS: U2.30, U5.1
FLASH_SDI: U2.33, U5.5
FLASH_SDO: U2.32, U5.2
FLASH_SHD: U2.28, U5.7
FLASH_SWP: U2.29, U5.3
FLASH_VDD: C24.1, SJ3.1, U2.26
GND: C3.1, C4.1, C5.1, C6.2, C7.2, C9.1, C10.2, C11.2, C12.2, C13.2, C14.2, C15.2, C16.2, C17.2, C18.2, C19.2, C20.2, C21.2, C22.2, C23.2, C24.2, C25.2, C26.1, C28.2, D3.C, E1.GND, E1.GND2, J1.1, J1.4, J2.1, J2.4, J2.20, JP2.1, JP15.GND, L1.2, R5.1, R6.1, R7.1, R8.1, S1.1, S1.2, S2.1, S2.2, U1.2, U2.EP, U3.2, U4.6, U4.16, U5.4, Y1.2, Y1.4
LNA_IN: C8.1, L1.1, U2.2
unnamed: D4.C, R8.2
unnamed: D3.A, R4.2
unnamed: R4.1, SJ2.1
unnamed: C27.2, R2.1, U2.47
unnamed: R13.2, U4.12
unnamed: R14.2, U4.11
unnamed: D1.C, U1.1
unnamed: Q2.5, R17.2
unnamed: C17.1, SJ3.2, U5.8
unnamed: Q2.2, R18.2
unnamed: C3.2, U2.45, Y1.1
unnamed: R5.2, SJ1.2, U1.5
unnamed: C4.2, U2.44, Y1.3
unnamed: R6.2, SJ1.1
unnamed: D1.A, R3.2
RTS: Q2.4, R18.1, U4.2
SHIELD: JP15.SHIELD1, JP15.SHIELD2, JP15.SHIELD3
TRACE_ANT: C8.2, C28.1, E1.ANT
U0RXD: J2.17, U2.40, U4.20
U0TXD: J2.18, U2.41, U4.4
VIN: C7.1, D2.C, Q1.2, U3.1, U3.3
VUSB-RAW: C11.1, F1.1, J1.2, J2.2, JP15.VBUS
V_BATT: C6.1, J1.3, J2.3, JP2.2, Q1.3, U1.3
V_USB: C14.1, C15.1, C19.1, D2.A, F1.2, Q1.1, R3.1, R7.2, U1.4, U4.15

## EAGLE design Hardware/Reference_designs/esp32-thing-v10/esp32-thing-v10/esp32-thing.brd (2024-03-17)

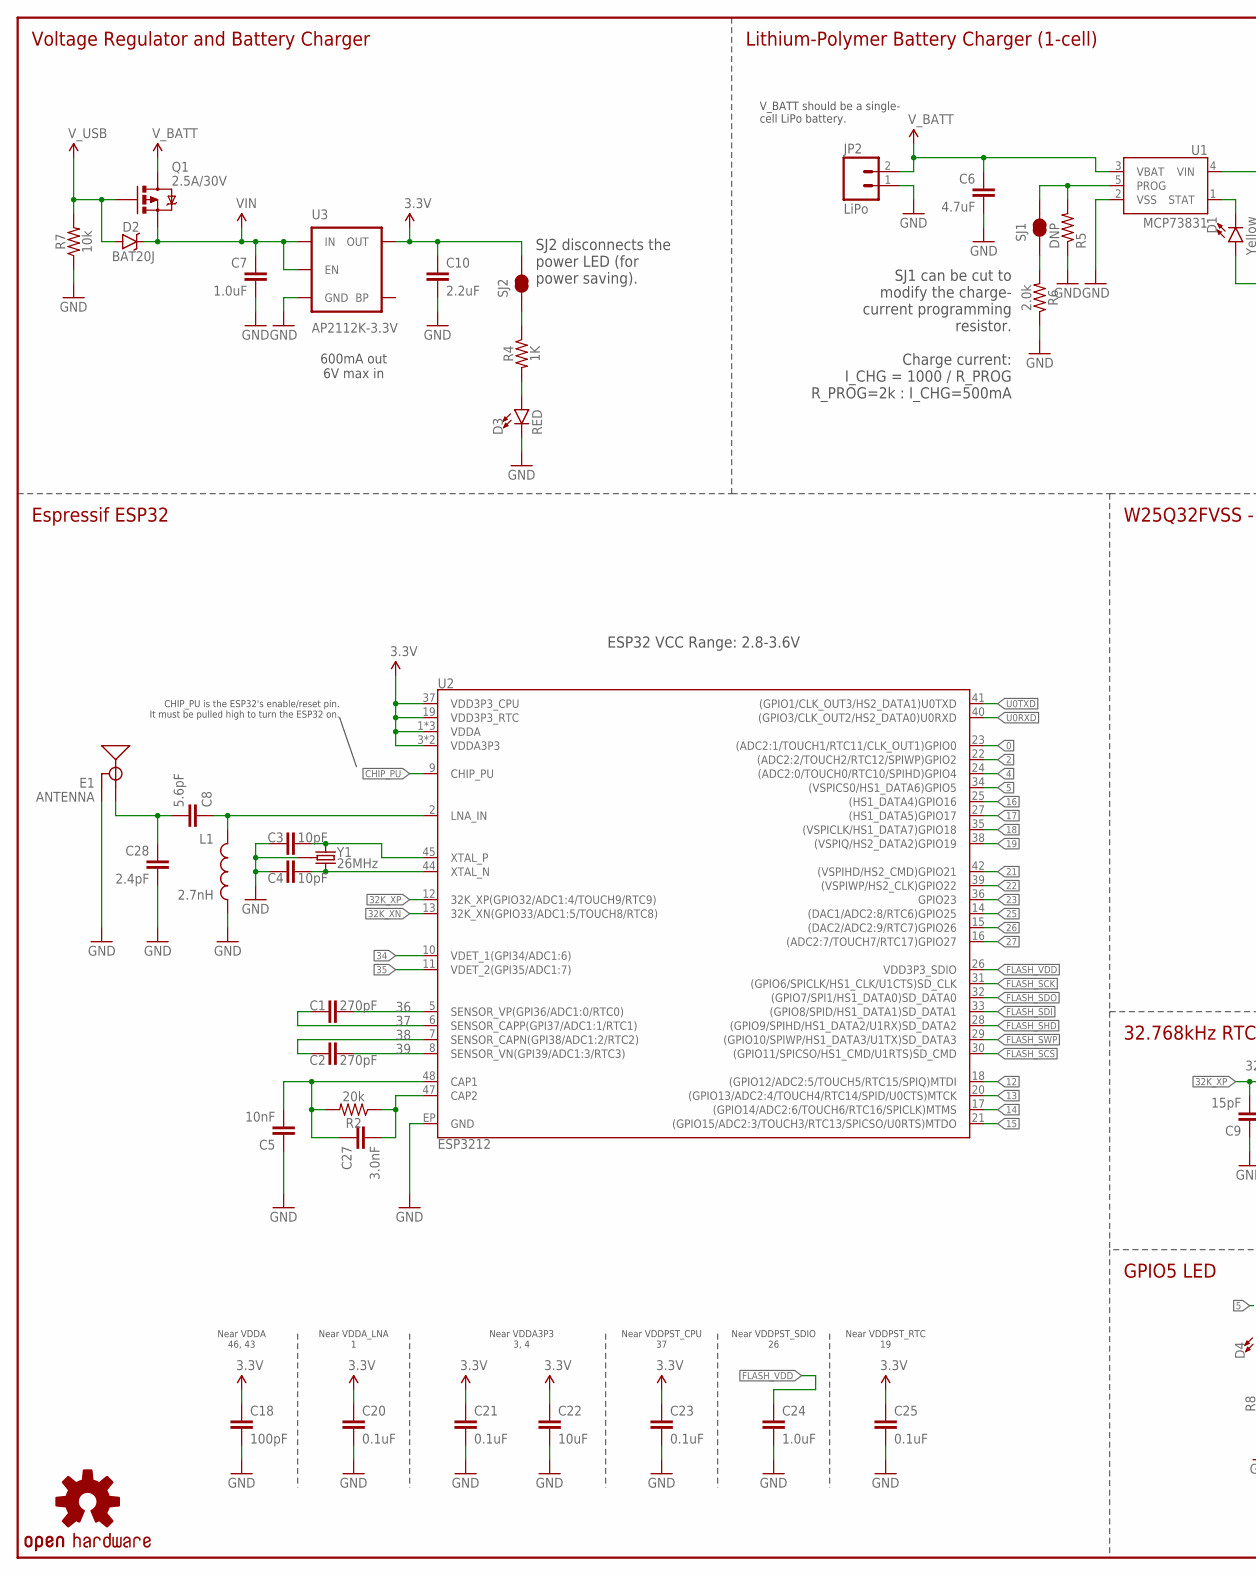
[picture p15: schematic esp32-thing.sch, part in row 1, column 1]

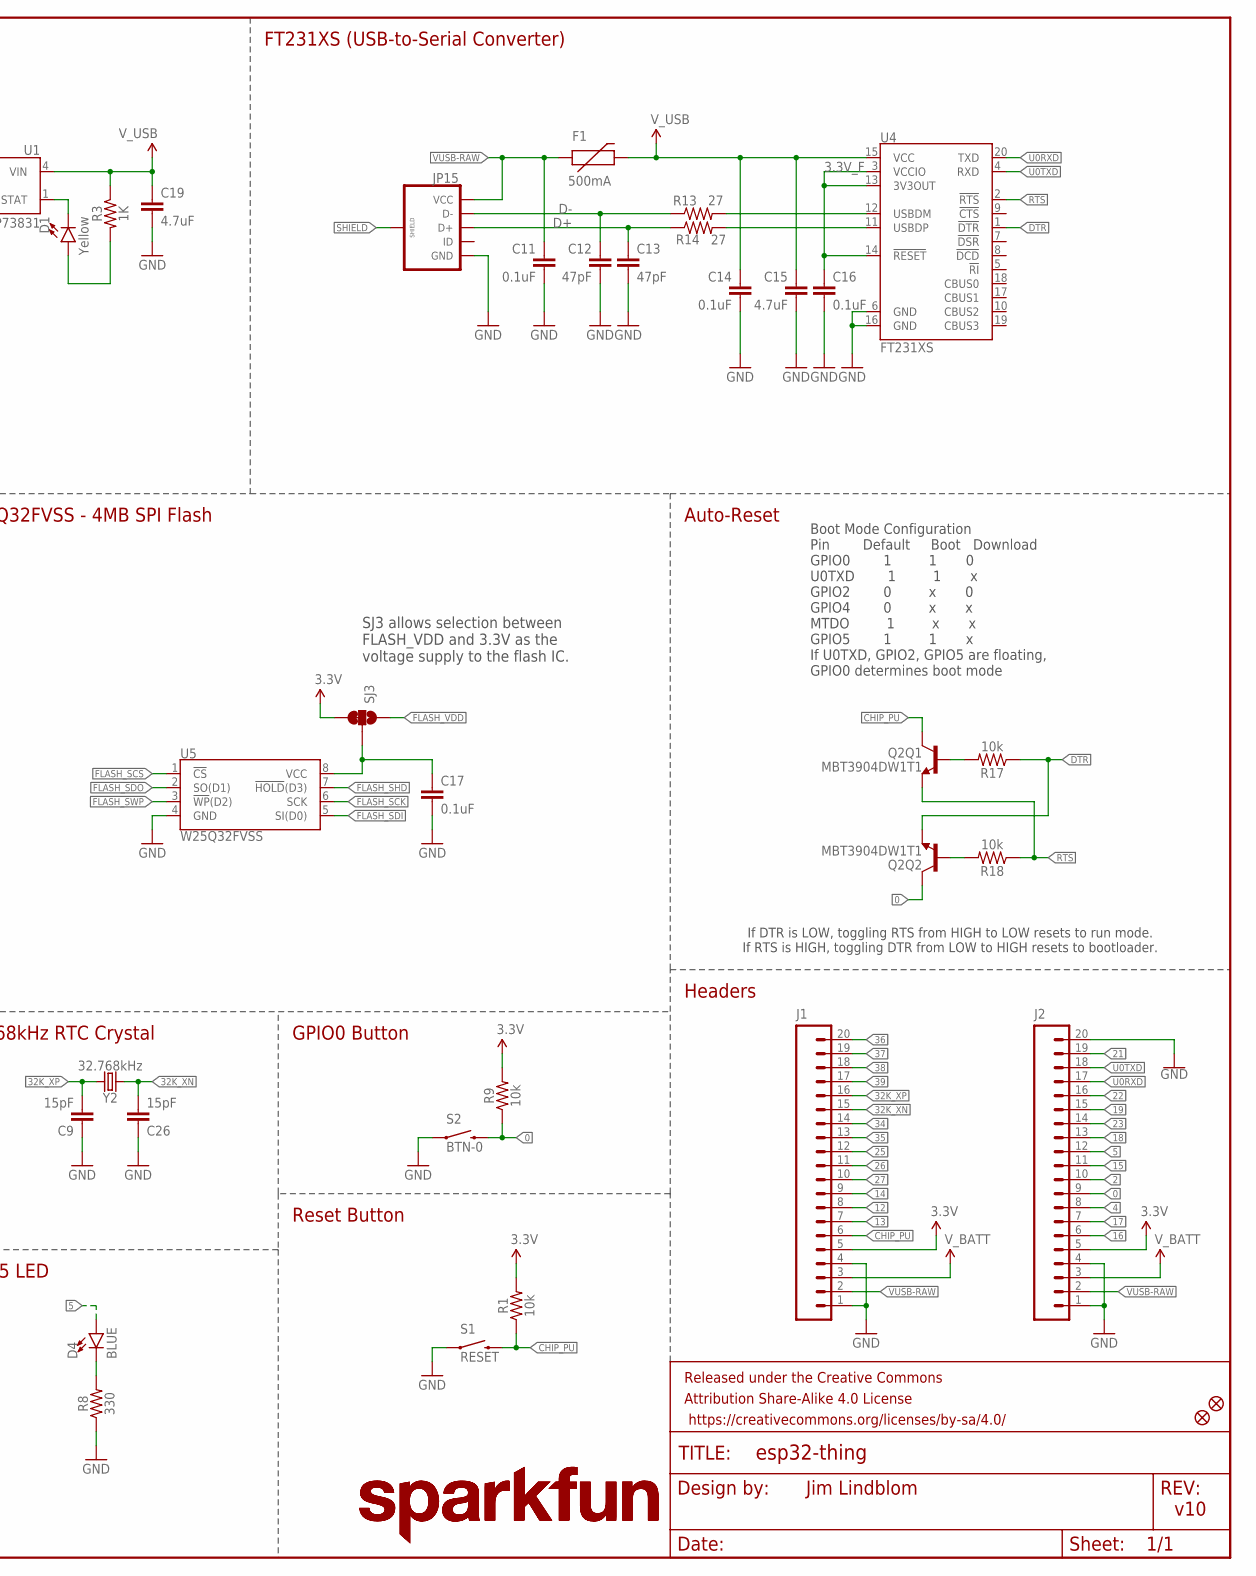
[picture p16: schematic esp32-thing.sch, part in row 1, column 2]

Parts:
C1, C2: 270pF; 0603
C3, C4: 10pF; 0603
C5: 10nF; 0603
C6, C19: 4.7uF; 0603
C7: 1.0uF; 0805
C8: 5.6pF; 0603
C9, C26: 15pF; 0603
C10: 2.2uF; 0603
C11, C14, C16, C17, C20, C21, C23, C25: 0.1uF; 0603
C12, C13: 47pF; 0603
C15: 4.7uF; 0603-CAP
C18: 100pF; 0603
C22: 10uF; 0603
C24: 1.0uF; 0603
C27: 3.0nF; 0603
C28: 2.4pF; 0603
D1: Yellow; LED-0603
D2: BAT20J; SOD-323
D3: RED; LED-0603
D4: BLUE; LED-0603
E1: ANTENNA; TRACE_ANTENNA_2.4GHZ_25.7MM_TUNED
F1: 500mA; PTC-1206
FD1, FD2: FIDUCIALUFIDUCIAL; MICRO-FIDUCIAL
FRAME1: FRAME-LEDGER; CREATIVE_COMMONS
J1, J2: M20NOSILK; 1X20_NOSILK
JP2: LiPo; JST-2-PTH
JP15: USB_MICROB_PLUGCONN-11752; USB-B-MICRO-SMD_V03
L1: 2.7nH; 0603
LOGO1, LOGO3: SFE_LOGO_NAME.2_INCH; SFE_LOGO_NAME_.2
LOGO2: OSHW-LOGOMINI; OSHW-LOGO-MINI
Q1: 2.5A/30V; SOT23-3
Q2: MBT3904DW1T1; SC70-6
R1, R7, R9, R17, R18: 10k; 0603
R2: 20k; 0603
R3, R4: 1K; 0603
R5: DNP; 1/6W-RES
R6: 2.0k; 0603
R8: 330; 0603
R13, R14: 27; 0603
S1: RESET; TACTILE_SWITCH_SMD_4.6X2.8MM
S2: BTN-0; TACTILE_SWITCH_SMD_4.6X2.8MM
SJ1, SJ2: JUMPER-PAD-2-NC_BY_TRACE; PAD-JUMPER-2-NC_BY_TRACE_YES_SILK
SJ3: JUMPER-PAD-3-2OF3_NC_BY_TRACE_SMALL; PAD-JUMPER-3-2OF3_NC_BY_TRACE_YES_SILK_FULL_BOX
U1: MCP73831; SOT23-5
U2: ESP3212; QFN48-0.4MM
U3: AP2112K-3.3V; SOT23-5
U4: FT231XS; SSOP20_L
U5: W25Q32FVSS; SOIC-8
Y1: 26MHz; CRYSTAL-SMD-3.2X2.5
Y2: 32.768kHz; CRYSTAL-SMD-3.2X1.5MM

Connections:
0: J2.9, Q2.6 (C), R9.1, S2.3 (2), S2.4 (2), U2.23 ((ADC2:1/TOUCH1/RTC11/CLK_OUT1)GPIO0)
2: J2.10, U2.22 ((ADC2:2/TOUCH2/RTC12/SPIWP)GPIO2)
3.3V: C10.1, C18.1, C20.1, C21.1, C22.1, C23.1, C25.1, J1.5, J2.5, R1.2, R9.2, SJ2.2, SJ3.3, U2.1 (VDDA), U2.3 (VDDA3P3), U2.4 (VDDA3P3), U2.19 (VDD3P3_RTC), U2.37 (VDD3P3_CPU), U2.43 (VDDA), U2.46 (VDDA), U3.5 (OUT)
3.3V_F: C16.1, U4.3 (VCCIO), U4.13 (3V3OUT), U4.14 (!RESET)
4: J2.8, U2.24 ((ADC2:0/TOUCH0/RTC10/SPIHD)GPIO4)
5: D4.A, J2.12, U2.34 ((VSPICS0/HS1_DATA6)GPIO5)
12: J1.8, U2.18 ((GPIO12/ADC2:5/TOUCH5/RTC15/SPIQ)MTDI)
13: J1.7, U2.20 ((GPIO13/ADC2:4/TOUCH4/RTC14/SPID/U0CTS)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)
14: J1.9, U2.17 ((GPIO14/ADC2:6/TOUCH6/RTC16/SPICLK)MTMS)
15: J2.11, U2.21 ((GPIO15/ADC2:3/TOUCH3/RTC13/SPICSO/U0RT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)
16: J2.6, U2.25 ((HS1_DATA4)GPIO16)
17: J2.7, U2.27 ((HS1_DATA5)GPIO17)
18: J2.13, U2.35 ((VSPICLK/HS1_DATA7)GPIO18)
19: J2.15, U2.38 ((VSPIQ/HS2_DATA2)GPIO19)
21: J2.19, U2.42 ((VSPIHD/HS2_CMD)GPIO21)
22: J2.16, U2.39 ((VSPIWP/HS2_CLK)GPIO22)
23: J2.14, U2.36 (GPIO23)
25: J1.12, U2.14 ((DAC1/ADC2:8/RTC6)GPIO25)
26: J1.11, U2.15 ((DAC2/ADC2:9/RTC7)GPIO26)
27: J1.10, U2.16 ((ADC2:7/TOUCH7/RTC17)GPIO27)
32K_XN: C26.2, J1.15, U2.13 (32K_XN(GPIO33/ADC1:5/TOUCH8/RTC8)), Y2.P$2 (2)
32K_XP: C9.2, J1.16, U2.12 (32K_XP(GPIO32/ADC1:4/TOUCH9/RTC9)), Y2.P$1 (1)
34: J1.14, U2.10 (VDET_1(GPI34/ADC1:6))
35: J1.13, U2.11 (VDET_2(GPI35/ADC1:7))
36: C1.2, J1.20, U2.5 (SENSOR_VP(GPI36/ADC1:0/RTC0))
37: C1.1, J1.19, U2.6 (SENSOR_CAPP(GPI37/ADC1:1/RTC1))
38: C2.1, J1.18, U2.7 (SENSOR_CAPN(GPI38/ADC1:2/RTC2))
39: C2.2, J1.17, U2.8 (SENSOR_VN(GPI39/ADC1:3/RTC3))
CAP_10N: C5.2, C27.1, R2.2, U2.48 (CAP1)
CHIP_PU: J1.6, Q2.3 (C), R1.1, S1.3 (2), S1.4 (2), U2.9 (CHIP_PU)
D+: C13.1, JP15.D+, R14.1
D-: C12.1, JP15.D-, R13.1
DTR: Q2.1 (E), R17.1, U4.1 (!DTR)
FLASH_SCK: U2.31 ((GPIO6/SPICLK/HS1_CLK/U1CTS)SD_CLK), U5.6 (SCK)
FLASH_SCS: U2.30 ((GPIO11/SPICSO/HS1_CMD/U1RTS)SD_CMD), U5.1 (!CS!)
FLASH_SDI: U2.33 ((GPIO8/SPID/HS1_DATA1)SD_DATA1), U5.5 (SI(D0))
FLASH_SDO: U2.32 ((GPIO7/SPI1/HS1_DATA0)SD_DATA0), U5.2 (SO(D1))
FLASH_SHD: U2.28 ((GPIO9/SPIHD/HS1_DATA2/U1RX)SD_DATA2), U5.7 (!HOLD!(D3))
FLASH_SWP: U2.29 ((GPIO10/SPIWP/HS1_DATA3/U1TX)SD_DATA3), U5.3 (!WP!(D2))
FLASH_VDD: C24.1, SJ3.1, U2.26 (VDD3P3_SDIO)
GND: C3.1, C4.1, C5.1, C6.2, C7.2, C9.1, C10.2, C11.2, C12.2, C13.2, C14.2, C15.2, C16.2, C17.2, C18.2, C19.2, C20.2, C21.2, C22.2, C23.2, C24.2, C25.2, C26.1, C28.2, D3.C, E1.GND, E1.GND2 (GND), J1.1, J1.4, J2.1, J2.4, J2.20, JP2.1, JP15.GND, L1.2, R5.1, R6.1, R7.1, R8.1, S1.1, S1.2 (1), S2.1, S2.2 (1), U1.2 (VSS), U2.EP (GND), U3.2 (GND), U4.6 (GND), U4.16 (GND), U5.4 (GND), Y1.2 (GND), Y1.4 (GND)
LNA_IN: C8.1, L1.1, U2.2 (LNA_IN)
unnamed: D4.C, R8.2
unnamed: D3.A, R4.2
unnamed: R4.1, SJ2.1
unnamed: C27.2, R2.1, U2.47 (CAP2)
unnamed: R13.2, U4.12 (USBDM)
unnamed: R14.2, U4.11 (USBDP)
unnamed: D1.C, U1.1 (STAT)
unnamed: Q2.5 (B), R17.2
unnamed: C17.1, SJ3.2, U5.8 (VCC)
unnamed: Q2.2 (B), R18.2
unnamed: C3.2, U2.45 (XTAL_P), Y1.1
unnamed: R5.2, SJ1.2, U1.5 (PROG)
unnamed: C4.2, U2.44 (XTAL_N), Y1.3 (2)
unnamed: R6.2, SJ1.1
unnamed: D1.A, R3.2
RTS: Q2.4 (E), R18.1, U4.2 (!RTS)
SHIELD: JP15.SHIELD1 (SHIELD), JP15.SHIELD2 (SHIELD), JP15.SHIELD3 (SHIELD)
TRACE_ANT: C8.2, C28.1, E1.ANT (SIGNAL)
U0RXD: J2.17, U2.40 ((GPIO3/CLK_OUT2/HS2_DATA0)U0RXD), U4.20 (TXD)
U0TXD: J2.18, U2.41 ((GPIO1/CLK_OUT3/HS2_DATA1)U0TXD), U4.4 (RXD)
VIN: C7.1, D2.C, Q1.2 (S), U3.1 (IN), U3.3 (EN)
VUSB-RAW: C11.1, F1.1, J1.2, J2.2, JP15.VBUS (VCC)
V_BATT: C6.1, J1.3, J2.3, JP2.2, Q1.3 (D), U1.3 (VBAT)
V_USB: C14.1, C15.1, C19.1, D2.A, F1.2, Q1.1 (G), R3.1, R7.2, U1.4 (VIN), U4.15 (VCC)

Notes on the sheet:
Boot Mode Configuration Pin Default Boot Download GPIO0 1 1 0 U0TXD 1 1 x GPIO2 0 x 0 GPIO4 0 x x MTDO 1 x x GPIO5 1 1 x If U0TXD, GPIO2, GPIO5 are floating, GPIO0 determines boot mode
FT231XS (USB-to-Serial Converter)
V_BATT should be a single- cell LiPo battery.
Charge current: I_CHG = 1000 / R_PROG R_PROG=2k : I_CHG=500mA
Voltage Regulator and Battery Charger
SJ1 can be cut to modify the charge- current programming resistor.
Lithium-Polymer Battery Charger (1-cell)
600mA out 6V max in
Auto-Reset
Near VDDA 46, 43
Near VDDA_LNA 1
Near VDDA3P3 3, 4
Near VDDPST_CPU 37
Near VDDPST_SDIO 26
Near VDDPST_RTC 19
Espressif ESP32
W25Q32FVSS - 4MB SPI Flash
32.768kHz RTC Crystal
GPIO0 Button
Reset Button
GPIO5 LED
Headers
v10
Jim Lindblom
ESP32 VCC Range: 2.8-3.6V
SJ3 allows selection between FLASH_VDD and 3.3V as the voltage supply to the flash IC.
SJ2 disconnects the power LED (for power saving).
If DTR is LOW, toggling RTS from HIGH to LOW resets to run mode. If RTS is HIGH, toggling DTR from LOW to HIGH resets to bootloader.
CHIP_PU is the ESP32's enable/reset pin. It must be pulled high to turn the ESP32 on.

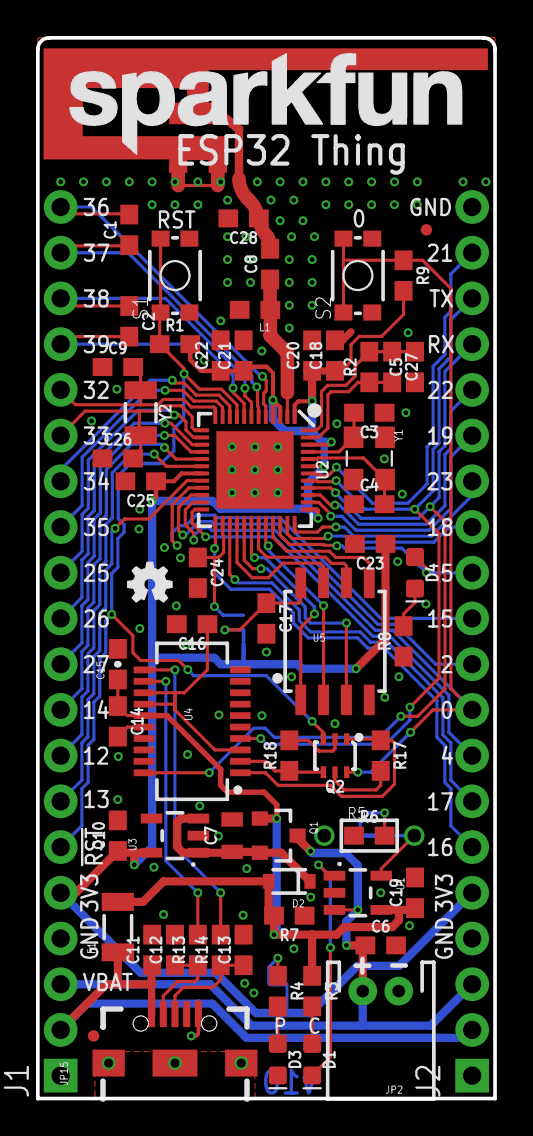
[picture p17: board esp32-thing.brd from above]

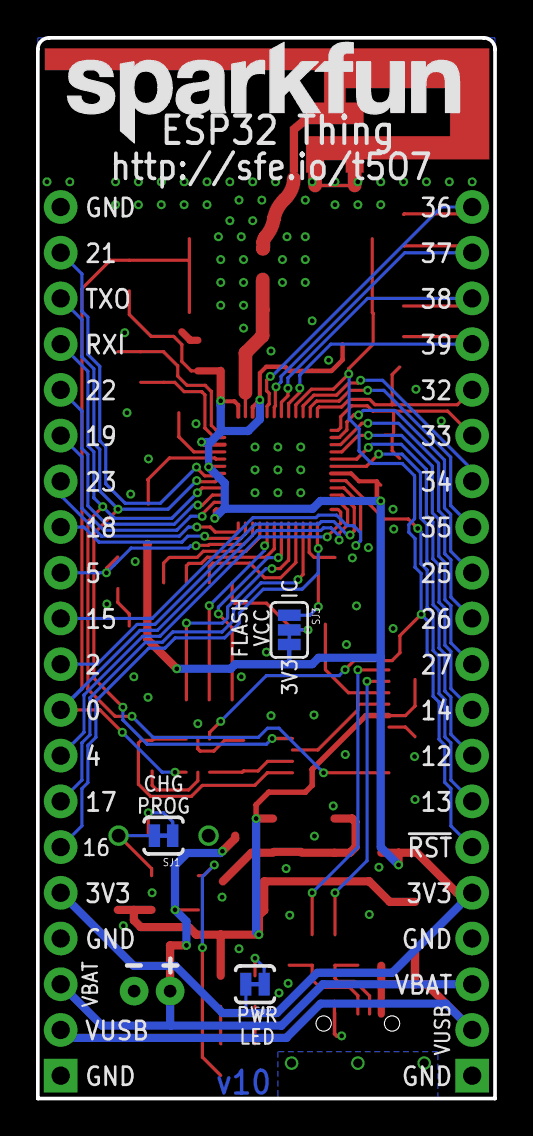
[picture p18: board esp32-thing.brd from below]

Board: 2 copper layers, 25.4 x 58.9 mm, 72 parts (4 on the bottom side), 66 nets.

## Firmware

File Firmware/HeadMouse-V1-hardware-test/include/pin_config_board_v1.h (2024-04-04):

/* CIRCUIT BOARD V1 PIN CONFIG *********************************************/
/* 
/* Description: This is a hardware pin config file for HeadMouse board version 1.
/* Author: Vanessa Prankl
/* Date: 26.03.2024
/* 
/************************************************************************/
#pragma once
#include <Arduino.h>

/* LEDs */
const int8_t PIN_LED_BAT_R = 6;
const int8_t PIN_LED_BAT_G = 7;
const int8_t PIN_LED_STATUS_R = 17;
const int8_t PIN_LED_STATUS_G = 18;

/* Buttons */
const int8_t PIN_BTN_1 = 42;
const int8_t PIN_BTN_2 = 41;
const int8_t PIN_BTN_3 = 40;
const int8_t PIN_BTN_4 = 39;

/* Battery */
const int8_t PIN_VBATT_MEASURE = 4;     /* Current battery voltage */
const int8_t PIN_BATT_STATUS = 5;       /* Pulled low if charging is active*/

/* I2C */
const int8_t PIN_I2C_SCL = 9;
const int8_t PIN_I2C_SDA = 10;

/* IMU interrupt pins */
const int8_t PIN_LSM6DS_INT = 11;
const int8_t PIN_MC6470_INT = 12;
const int8_t PIN_BNO55_INT = 13;

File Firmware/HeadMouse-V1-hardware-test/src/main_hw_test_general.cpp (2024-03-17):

/* HARDWARE TEST HEADMOUSE V1 *******************************************/
/* 
/* Description: This is a hardware test firmware for HeadMouse board version 1.
/* Author: Vanessa Prankl
/* Date: 11.01.2024
/* 
/************************************************************************/
#ifdef HW_TEST 
#include <Arduino.h>
#include <Wire.h>

/* PIN DEFINITIONS ******************************************************/
const int8_t PIN_LED_BAT_R = 6;
const int8_t PIN_LED_BAT_G = 7;
const int8_t PIN_LED_STATUS_R = 17;
const int8_t PIN_LED_STATUS_G = 18;

const int8_t PIN_BTN_1 = 42;
const int8_t PIN_BTN_2 = 41;
const int8_t PIN_BTN_3 = 40;
const int8_t PIN_BTN_4 = 39;

const int8_t PIN_VBATT_MEASURE = 4;     /* Current battery voltage */
const int8_t PIN_BATT_STATUS = 5;       /* Pulled low if charging is active*/

const int8_t PIN_I2C_SCL = 9;
const int8_t PIN_I2C_SDA = 10;
const int8_t PIN_LSM6DS_INT = 11;
const int8_t PIN_MC6470_INT = 12;
const int8_t PIN_BNO55_INT = 13;

/* FUNCTION DEFINITIONS **************************************************/
void i2c_bus_scan(){
  byte error, address;
  int nDevices;
  Serial.println("\n=== I2C Scanner ===");
  nDevices = 0;
  for (address = 1; address < 127; address++ )
  {
    Wire.beginTransmission(address);
    error = Wire.endTransmission();

    if (error == 0)
    {
      Serial.print("Device at address: 0x");
      if (address < 16) Serial.print("0");
      Serial.print(address, HEX);
      Serial.println("");
      nDevices++;
    }
    else if (error == 4)
    {
      Serial.print("Unknown error at address: 0x");
      if (address < 16) Serial.print("0");
      Serial.println(address, HEX);
    }
  }
  if (nDevices == 0) Serial.println("No I2C devices found\n");
  else Serial.println("I2C scan finished\n");
}

void button_test(){
  bool button_1 = digitalRead(PIN_BTN_1);
  bool button_2 = digitalRead(PIN_BTN_2);
  bool button_3 = digitalRead(PIN_BTN_3);
  bool button_4 = digitalRead(PIN_BTN_4);

  Serial.print("Button values: ");
  Serial.print(button_1);
  Serial.print(", ");
  Serial.print(button_2);
  Serial.print(", ");
  Serial.print(button_3);
  Serial.print(", ");
  Serial.println(button_4);
}

void battery_measurement_test(){
  bool battery_charging = digitalRead(PIN_BATT_STATUS);
  int32_t adc_value = analogRead(PIN_VBATT_MEASURE);
  float_t battery_voltage = adc_value * 3.3 / 4095;

  Serial.print("Battery charging status: ");
  Serial.println(!battery_charging);
  Serial.print("Battery voltage: ");
  Serial.println(battery_voltage);
}

void led_test(){
  digitalWrite(PIN_LED_BAT_R, HIGH);  
  digitalWrite(PIN_LED_BAT_G, LOW); 
  digitalWrite(PIN_LED_STATUS_R, HIGH);  
  digitalWrite(PIN_LED_STATUS_G, LOW);  

  delay(500);         

  digitalWrite(PIN_LED_BAT_R, LOW);  
  digitalWrite(PIN_LED_BAT_G, HIGH);  
  digitalWrite(PIN_LED_STATUS_R, LOW);  
  digitalWrite(PIN_LED_STATUS_G, HIGH);

  delay(500);         

  digitalWrite(PIN_LED_BAT_R, LOW);  
  digitalWrite(PIN_LED_BAT_G, LOW);  
  digitalWrite(PIN_LED_STATUS_R, LOW);  
  digitalWrite(PIN_LED_STATUS_G, LOW);
}

/* INIT *****************************************************************/
void setup() {

  Serial.begin(9600);

  /* Init LEDs */
  pinMode(PIN_LED_BAT_R, OUTPUT);
  pinMode(PIN_LED_BAT_G, OUTPUT);
  pinMode(PIN_LED_STATUS_R, OUTPUT);
  pinMode(PIN_LED_STATUS_G, OUTPUT);

  /* Init Buttons */
  pinMode(PIN_BTN_1, INPUT_PULLUP);
  pinMode(PIN_BTN_2, INPUT_PULLUP);
  pinMode(PIN_BTN_3, INPUT_PULLUP);
  pinMode(PIN_BTN_4, INPUT_PULLUP);  
  
  /* Init battery measurements */
  pinMode(PIN_BATT_STATUS, INPUT_PULLUP);

  /* Init I2C (IMUs) */
  Wire.begin(PIN_I2C_SDA, PIN_I2C_SCL, 400000);

  delay(5000); 
}

/* MAIN ******************************************************************/
void loop() {

  i2c_bus_scan();

  button_test();

  battery_measurement_test();

  led_test();

  delay(1000);       
}
#endif

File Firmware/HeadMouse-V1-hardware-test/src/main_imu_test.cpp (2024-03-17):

/* HARDWARE TEST HEADMOUSE V1 *******************************************/
/* 
/* Description: This is an IMU test firmware for HeadMouse board version 1.
/* Author: Vanessa Prankl
/* Date: 06.02.202
/*
/* IMUs under test: MC6470, LSM6DSO, BNO055
/* 
/************************************************************************/
#include <Arduino.h>
#include <Wire.h>
#include "SparkFunLSM6DSO.h"

/* PIN DEFINITIONS ******************************************************/
const int8_t PIN_I2C_SCL = 9;
const int8_t PIN_I2C_SDA = 10;
const int8_t PIN_LSM6DS_INT = 11;
const int8_t PIN_MC6470_INT = 12;
const int8_t PIN_BNO55_INT = 13;

LSM6DSO lsm6dso;


/* FUNCTION PROTOTYPES **************************************************/
void i2c_bus_scan();


/* INIT *****************************************************************/
void setup() {

  Serial.begin(9600);

  /* Init I2C */
  Wire.begin(PIN_I2C_SDA, PIN_I2C_SCL, 400000);
  delay(10);  /* Let I2C bus come up */

  /* Init LSM6DSO IMU */
  if(lsm6dso.begin(0x6A, Wire)){
    Serial.println("LSM6DSO ready");
  }
  else{
    Serial.println("LSM6DSO not reachable");
  }

  if(lsm6dso.initialize(BASIC_SETTINGS)){
    Serial.println("LSM6DSO initialized");
  }
  else{
    Serial.println("Canno init LSM6DSO");
  }

  delay(5000); 

  i2c_bus_scan();
}


/* MAIN ******************************************************************/
void loop() {

  /* Read LSM6DSO IMU params */
  Serial.print("\nAccelerometer:\n");
  Serial.print(" X = ");
  Serial.println(lsm6dso.readFloatAccelX(), 3);
  Serial.print(" Y = ");
  Serial.println(lsm6dso.readFloatAccelY(), 3);
  Serial.print(" Z = ");
  Serial.println(lsm6dso.readFloatAccelZ(), 3);

  Serial.print("\nGyroscope:\n");
  Serial.print(" X = ");
  Serial.println(lsm6dso.readFloatGyroX(), 3);
  Serial.print(" Y = ");
  Serial.println(lsm6dso.readFloatGyroY(), 3);
  Serial.print(" Z = ");
  Serial.println(lsm6dso.readFloatGyroZ(), 3);

  Serial.print("\nThermometer:\n");
  Serial.print(" Degrees F = ");
  Serial.println(lsm6dso.readTempF(), 3);

  delay(1000);       
}


/* FUNCTION DEFINITIONS **************************************************/
void i2c_bus_scan(){
  byte error, address;
  int nDevices;
  Serial.println("\n=== I2C Scanner ===");
  nDevices = 0;
  for (address = 1; address < 127; address++ )
  {
    Wire.beginTransmission(address);
    error = Wire.endTransmission();

    if (error == 0)
    {
      Serial.print("Device at address: 0x");
      if (address < 16) Serial.print("0");
      Serial.print(address, HEX);
      Serial.println("");
      nDevices++;
    }
    else if (error == 4)
    {
      Serial.print("Unknown error at address: 0x");
      if (address < 16) Serial.print("0");
      Serial.println(address, HEX);
    }
  }
  if (nDevices == 0) Serial.println("No I2C devices found\n");
  else Serial.println("I2C scan finished\n");
}

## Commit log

2023-11-20 First Schematic for Headmouse
    [690367280676.step, FC68125.step, FM3_mainboard.kicad_pcb, FM3_mainboard.kicad_sch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]
2023-11-20 Updated Comment
    [IMU.kicad_sch, Microcontroller.kicad_sch, untitled.kicad_sch]
2023-11-27 General schematic improvements
    - Replaced ESP32-WROOM by ESP32-S3-WROOM
    - Removed autonomous reboot option (not needed for ESP32-S3)
    - Added clock crystal footprint
    - Replaced USB-C version 3 with USB- v2 due to less connections
    - Added TVS-array to USB-C connector
    - Added inductance to USB-C connector for noise reduction
    [HM_mainboard.kicad_pcb, HM_mainboard.kicad_sch, IMU.kicad_sch, Microcontroller.kicad_sch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]
2023-11-27 Added TVS-Diodes for button jacks
    [UI_Peripherals.kicad_sch]
2023-11-27 Updated components of power supply unit
    - Replaced PMOSFET
    - Replaced LDO
    - Replaced battery charger
    - Replaced caps and resistors
    - Replaced battery connector
    [Microcontroller.kicad_sch, UI_Peripherals.kicad_sch, untitled.kicad_sch]
2023-11-28 Updated port connectors to new microcontroller
    [HM_mainboard.kicad_sch, untitled.kicad_sch]
2023-11-28 Updated port connectors of microcontroller
    [HM_mainboard.kicad_sch, IMU.kicad_sch, Microcontroller.kicad_sch, UI_Peripherals.kicad_sch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]
2023-12-02 Added IMUs, updated some components
    - Added 2 additonal IMUs:
    1) 6-Axis MC6470
    2) 9-Axis BNO55
    - Replaced button jack connectors
    - Replaced battery charging LED by a charging status measurement circuit
    - Replaced caps for clock crystal
    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
    [HM_mainboard.kicad_sch, IMU.kicad_sch, Microcontroller.kicad_sch, UI_Peripherals.kicad_sch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]
2023-12-03 Changed I2C address selection of IMUs
    [HM_mainboard.kicad_sch, IMU.kicad_sch, Microcontroller.kicad_sch, untitled.kicad_sch]
2023-12-03 Added pull-ups to i2c connections
    [HM_mainboard.kicad_sch, IMU.kicad_sch]
2023-12-03 Started component placement for PCB
    [HM_mainboard.kicad_pcb, HM_mainboard.kicad_sch, IMU.kicad_sch, Microcontroller.kicad_sch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]
2023-12-05 Updated footprint of auxiliary jacks, routed first version of PCB
    [HM_mainboard.kicad_pcb, HM_mainboard.kicad_sch, IMU.kicad_sch, UI_Peripherals.kicad_sch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]
2023-12-05 Added gerber and drill files
    [HM_mainboard-B_Cu.gbr, HM_mainboard-B_Mask.gbr, HM_mainboard-B_Paste.gbr, HM_mainboard-B_Silkscreen.gbr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]
2023-12-06 Added BOM
    [BOM_HM_mainboard.csv, HM_mainboard.kicad_pcb, IMU.kicad_sch, Microcontroller.kicad_sch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]
2023-12-11 Moved measurement lines. Updated PCB according to Aisler DRC
    [HM_mainboard.kicad_pcb, HM_mainboard.kicad_sch]
2023-12-11 Updated BOM
    [HM_mainboard.csv, HM_mainboard.kicad_pcb, IMU.kicad_sch, Microcontroller.kicad_sch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]
2023-12-13 Removed autosaved schematic
    [HM_mainboard.kicad_sch, Microcontroller.kicad_sch]
2024-01-18 Added hardware test firmware for board V1
2024-02-05 Replaced Arduino hardware test by platform io project
    [HM_mainboard.kicad_sch, Microcontroller.kicad_sch]
2024-03-17 Fixed wrong symbol-to-footprint assignment of PMOS AS3401
    [HM_mainboard.kicad_pcb, untitled.kicad_sch]
2024-03-17 Swapped battery polarity due to wrong pinning assumption
    Bugfix
    [HM_mainboard.kicad_pcb, untitled.kicad_sch]
2024-03-17 Fixed missing GND connections of BNO055 at Pin 15 and 16
    Bugfix due to wrong pin assignments in symbol library
    [HM_mainboard.kicad_pcb, IMU.kicad_sch]
2024-03-17 Added testpoints to pcb
    [HM_mainboard.kicad_pcb, IMU.kicad_sch, Microcontroller.kicad_sch, UI_Peripherals.kicad_sch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]
2024-03-17 Added gerber files and schematic printed to pdf
    [HM_mainboard-B_Cu.gbr, HM_mainboard-B_Mask.gbr, HM_mainboard-B_Paste.gbr, HM_mainboard-B_Silkscreen.gbr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]
2024-03-28 Fixed temperature measurement issue
2024-03-28 Improved pcb layout design
    [HM_mainboard.kicad_pcb]
2024-04-08 Moved a wire
    [HM_mainboard.kicad_pcb]
2024-04-11 Added connector for sip&puff sensor
    [HM_mainboard.kicad_pcb, HM_mainboard.kicad_sch, IMU.kicad_sch, UI_Peripherals.kicad_sch]
2024-04-11 Added BOM for V1.1.0
    [BOM_HM_mainboard_V1.0.0.ods, HM_mainboard.kicad_pcb]
2024-04-11 Added hardware version to PCB silkscreen
    [HM_mainboard.kicad_pcb]
2024-04-17 Updated schematic and PCB according to Email from BA on 16th of April
    [HM_mainboard.kicad_pcb, HM_mainboard.kicad_sch, IMU.kicad_sch, Microcontroller.kicad_sch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]
2024-04-18 Uniform text alignment
    [HM_mainboard.kicad_pcb]
2024-04-18 Added BOM for updated PCB-design; Added PDF-schematic
2024-05-15 Updated peripheral test program to calculate correct voltage from battery voltage measurement
2024-05-16 Updated peripheral test program to indicate battery charging status by led
2024-05-16 Added test documentation for pcb V1.1.1
2024-06-27 Added log level for battery logging
2024-06-27 Added default preferences for device config
2024-06-27 Added some major HeadMouse functions
    * device init
    * set preferences
    * get current BLE connection status
    * get current charging status
2024-06-27 Added IMU calibration check
2024-06-27 Added some log messages and IMU calibration check
2024-07-02 Added battery voltage levels for status description
2024-07-02 Added battery measurement and status description
2024-07-02 Added led types
2024-07-04 Finished battery status interpreter
2024-07-04 Finished device status interpreter
2024-07-09 Finished basic device status test.
2024-07-09 Updated log messages at init and debudged led state control
2024-07-14 Finished hardware timer- & pin change interrupt test
2024-07-17 Added LED implementation. Reorganized def files
2024-07-21 finalized hw timer implementation of LEDs. Removed multiple definiton linker error
2024-07-29 Updated schematic to version v2.0.0
    • Removed two 6-Axis IMUs
    • As the BNO055 did not respond to I2C requests, a 2k7 pullup was added in parallel to the I2C-SDA pullup. The behavior is described here: https://forums.adafruit.com/viewtopic.php?t=205215
    • Added mounting holes for enclosure
    • Added board description prints
    [HM_mainboard.kicad_pcb, HM_mainboard.kicad_sch, IMU.kicad_sch, Microcontroller.kicad_sch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]
2024-07-30 Added BOM, PDF and zipped V2.0.0 project data
    [BOM_HM_mainboard_V2.0.0.xlsx, HM_mainboard.kicad_pcb, IMU.kicad_sch, Microcontroller.kicad_sch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]
2024-08-01 Update ble connection mechanism. Multiple device can now be connected and auto reconnect was implemented
2024-08-04 Finished Bluetooth implementation. BLE repairs automatically and pairing can be invoked via button. No differentiation between manual pairing and connection lost pairing (device pairs to the next ava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
2024-08-08 Added hysteresis for battery level detection to prevent jitter when transitioning from one level to the other
2024-08-11 created 3D assembly of pcb board
    [HM_mainboard.kicad_pcb]
2024-08-12 Created bottom case
    [Case_bottom.SLDPRT]
2024-08-19 Finished bottom case design
    [Case_bottom.SLDPRT]
2024-08-19 Copied bottm case design as starting point for top case design
    [Case_top.SLDPRT]
2024-08-21 Finished first version of enclosure including 3D-print files
    [Case_bottom.3mf, Case_bottom.SLDPRT, Case_bottom.STEP, Case_top.3mf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]
2024-08-21 Improved enclosure print quality
    [Case_bottom.3mf, Case_bottom.SLDPRT, Case_bottom.STEP, Case_top.3mf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]
2024-08-21 finished Enclosure for HeadMouse PCB V2
    [Case_bottom.3mf, Case_bottom.SLDPRT, Case_bottom.STEP, Case_top.3mf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]
2024-08-23 Added connector for sip&puff sensor to enclosure
    [Case_bottom.SLDPRT, Case_bottom.STEP, Case_top.SLDPRT, Case_top.STEP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]
2024-08-31 Fixed wrong alignment issue in for-loop of LED library
2024-08-31 Added speed dependant sensitivtiy-ramp-up for detailed positioning of the mouse cursor and de-jitter
2024-10-14 Added program cycle timer for power saving

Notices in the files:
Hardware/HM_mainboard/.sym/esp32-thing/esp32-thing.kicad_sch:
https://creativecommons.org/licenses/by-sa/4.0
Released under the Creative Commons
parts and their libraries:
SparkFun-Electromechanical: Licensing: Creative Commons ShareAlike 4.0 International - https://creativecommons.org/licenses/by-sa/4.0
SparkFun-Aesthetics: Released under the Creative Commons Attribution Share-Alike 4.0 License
